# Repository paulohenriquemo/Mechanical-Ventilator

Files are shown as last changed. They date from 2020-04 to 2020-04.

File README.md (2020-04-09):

# Mechanical-Ventilator

Projeto de ventilador emergencial utilizando um Ressucitador manual (AMBU). Conforme o projeto for sendo encaminhado irei atualizando os arquivos.
Nova versão já em fase de testes! Basicamente os mesmos componentes em um layout mais adequado.
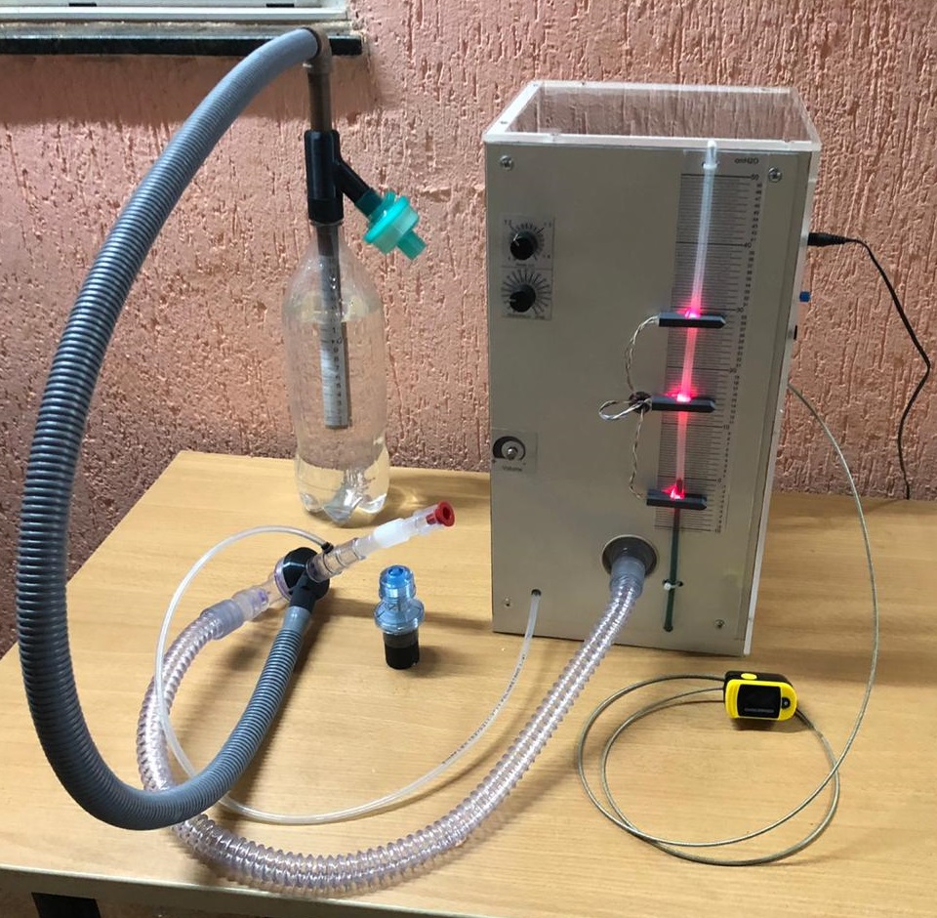
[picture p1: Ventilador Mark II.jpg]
Veltimador_MarkII


Diagrama do sistema:
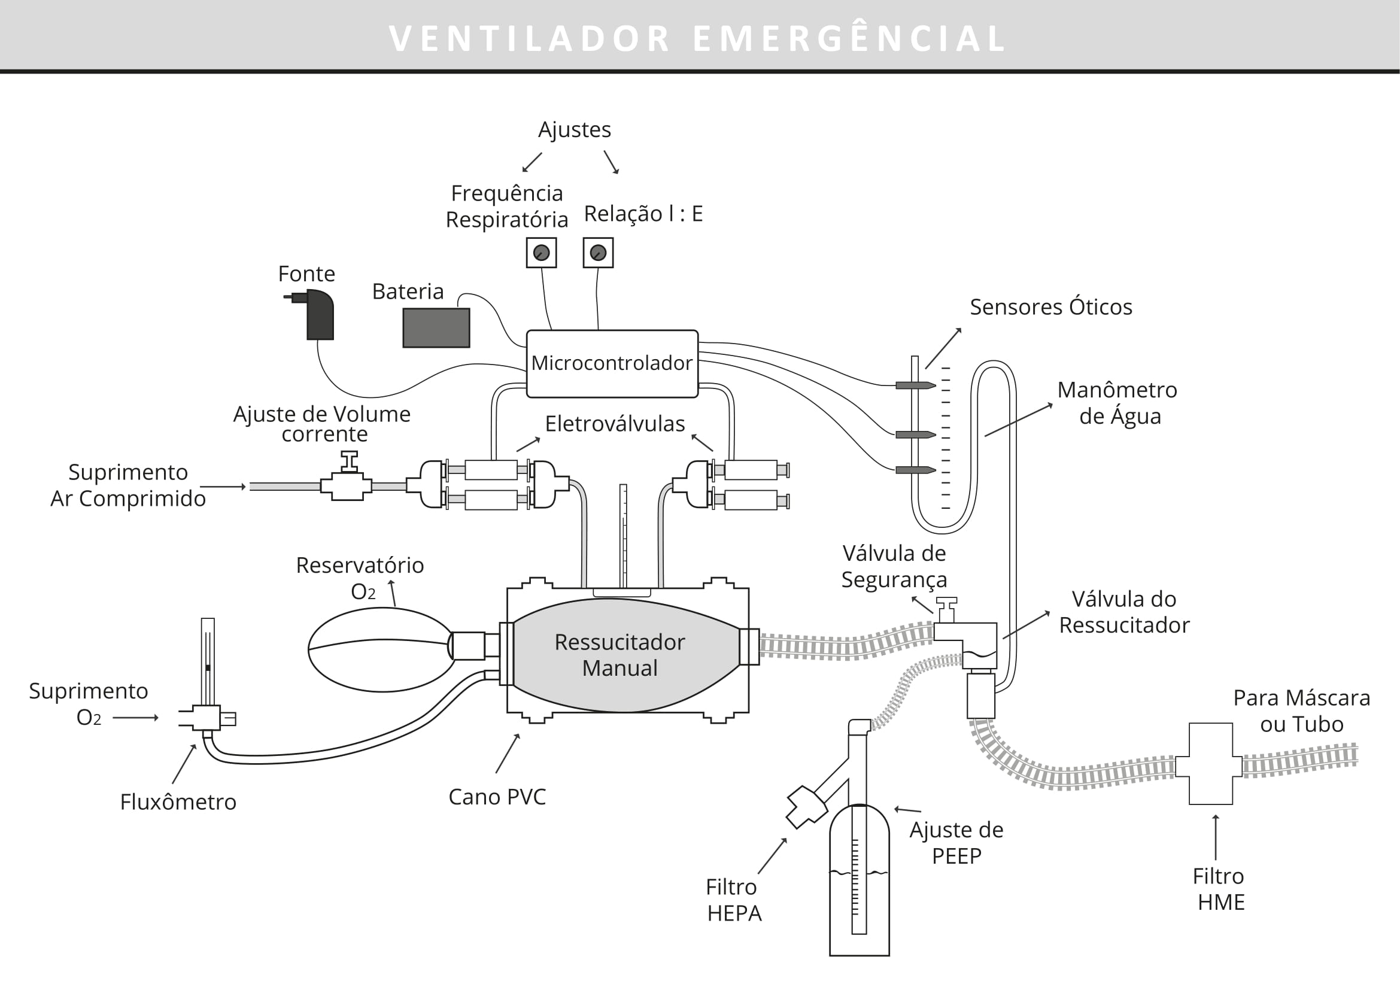
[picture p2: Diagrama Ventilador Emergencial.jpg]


Ilustração de uso:

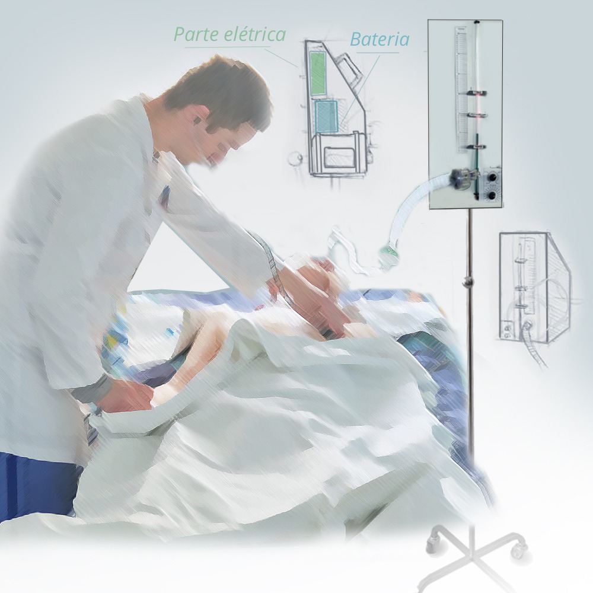
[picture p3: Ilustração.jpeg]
Ilustração de uso


Primeiro protótipo:

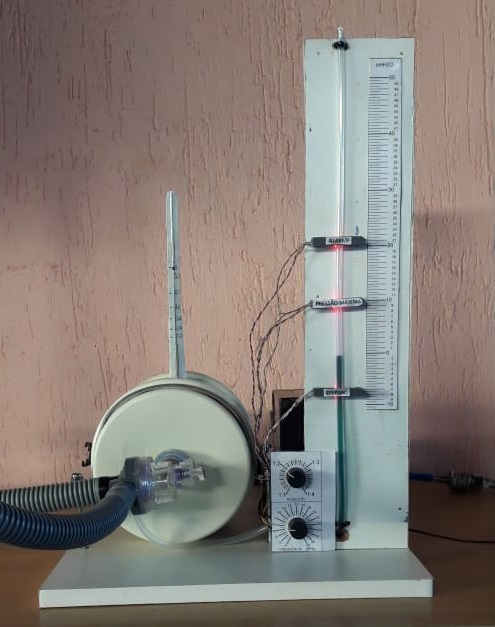
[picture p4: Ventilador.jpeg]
Primeiro Protótipo


Mais detalhes do projeto podem ser vistos no link https://www.youtube.com/watch?v=9hXmWFq5Jxk&feature=youtu.be

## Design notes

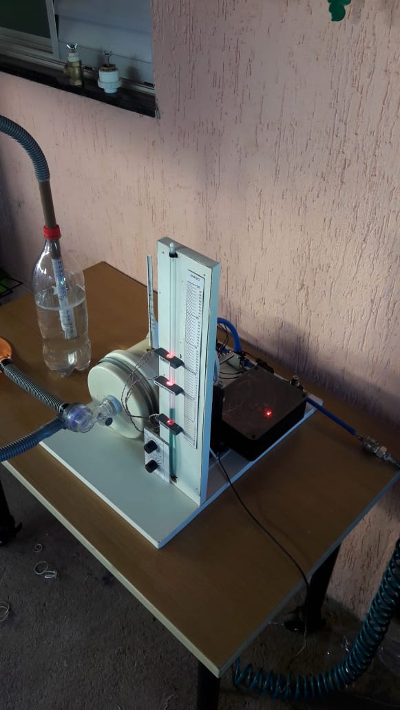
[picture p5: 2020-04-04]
Ventilador 2.jpeg

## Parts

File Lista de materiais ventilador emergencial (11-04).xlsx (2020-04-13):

 | Lista de Materiais para ventilador emergencial
QTD |  | VALOR UNIT | VALOR TOTAL | Referência
1 | AMBU | 230 | 230 | https://magazinemedica.com.br/produtos/visualiza/sku/8049/
1 | Adaptador para válvula PEEP | 30 | 30 | https://www.fibracirurgica.com.br/adaptador-diverter-md-para-conexao-da-valvula-peep-no-ambu/p
1 | Arduino Nano 5V | 25 | 25 | https://produto.mercadolivre.com.br/MLB-1242948735-arduino-nano-v30-5v-atmega328-p-au-_JM?quantity=1
4 | Mosfets | 1 | 4 | https://produto.mercadolivre.com.br/MLB-1321235515-modulo-mosfet-irf520-driver-controlador-p-motor-dc-arduino-_JM?quantity=1
1 | Resistores diversos (Conferir diagrama elétrico) | 2 | 2
4 | LDR 5mm | 0.25 | 1 | https://produto.mercadolivre.com.br/MLB-983516932-100-pecas-fotoresistor-ldr-5mm-pic-arduino-sensor-de-luz-_JM?quantity=1
4 | LED alto brilho vermelho 5mm | 0.1 | 0.4 | https://produto.mercadolivre.com.br/MLB-1433055648-1000x-led-vermelho-alto-brilho-5mm-kit-com-1000-pecas-_JM?quantity=1&variation=50510119992
2 | Potenciometro linear 10k | 1.2 | 2.4 | https://produto.mercadolivre.com.br/MLB-1081635890-potencimetro-10k-linear-com-eixo-l20-estriado-50-unidades-_JM?quantity=1
2 | Knob para potenciometro | 1.9 | 3.8 | https://produto.mercadolivre.com.br/MLB-1324374421-knob-6mm-preto-marcador-branco-p-potencimetro-10-pcs-_JM?quantity=1
1 | fonte 13v 1A | 32 | 32 | https://produto.mercadolivre.com.br/MLB-1305096440-fonte-p-televisor-colorido-13v-13a-bivolt-kairos-tcl1313-_JM?quantity=1
1 | push button pequeno | 1.8 | 1.8 | https://produto.mercadolivre.com.br/MLB-683849365-chave-push-button-na-vermelho-e-preta-pequeno-c10-unidades-_JM?quantity=1
1 | bateria 12V 7AH | 51 | 51 | https://produto.mercadolivre.com.br/MLB-1176479339-bateria-12v-7a-central-de-alarme-e-cerca-eletrica-nobreak-_JM?quantity=1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
1 | CAP 32mm Soldável | 1.5 | 1.5
1 | CAP 20mm Soldável | 0.5 | 0.5
1 | "T" 20mm Soldável | 0.5 | 0.5
1 | Luva de redução 32x35 Soldável | 3.5 | 3.5
1 | O'Ring de Silicone 20mm int por 4 esp | 3 | 3 | https://produto.mercadolivre.com.br/MLB-944957064-kit-oring-silicone-20-mm-especial-rinojosa-_JM?quantity=1
0.018 | tubo pvc soldável 25mm | 3 | 0.054
0.17 | tubo pvc soldável 20mm | 3 | 0.51
0.14 | tubo pvc soldável 32mm | 10 | 1.4
2 | Válvulas Solenoides | 65 | 130 | https://produto.mercadolivre.com.br/MLB-1061583637-solenoide-8mm-12v-vapor-gasolina-gazes-ar-agua-suspenso-_JM?quantity=1
2 | Tubo PU transparente 6mm ou 1/4'' | 2 | 4 | https://produto.mercadolivre.com.br/MLB-1291810963-rolo-de-25m-mangueira-pneumatica-tubo-pu-6mm-transparente-_JM
1 | Tubo PU 8mm | 3.5 | 3.5
1 | Regulador de fluxo 10mm | 14.7 | 14.7
1 | MDF para estrutura com fita de borda | 20 | 20
1 | Acrílico para lateral (45x22,5CM) | 6 | 6
1 | parafuso diversos | 10 | 10
1 | Fio Flexível para as coneções | 5 | 5
4 | Imas cubo 5mm | 0.5 | 2 | https://produto.mercadolivre.com.br/MLB-1335519560-neocube-cubo-magnetico-216-quadrados-im-neodimio-5mm-_JM?quantity=1&variation=44515493831
 | TOTAL |  | 589.564

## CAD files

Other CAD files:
planta respirador (1).dwg

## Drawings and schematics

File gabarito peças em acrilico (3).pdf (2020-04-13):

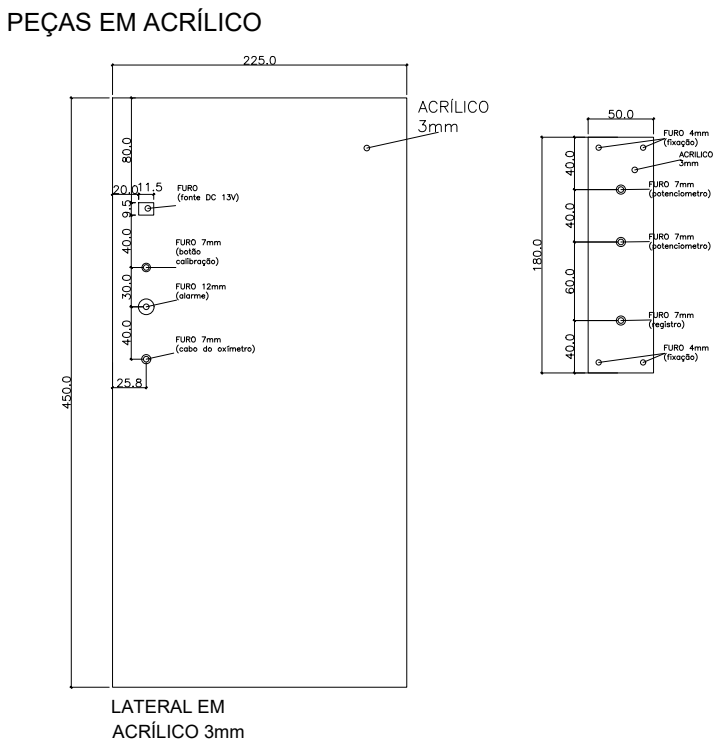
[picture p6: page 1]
LATERAL EM ACRÍLICO 3mm

PEÇAS EM ACRÍLICO

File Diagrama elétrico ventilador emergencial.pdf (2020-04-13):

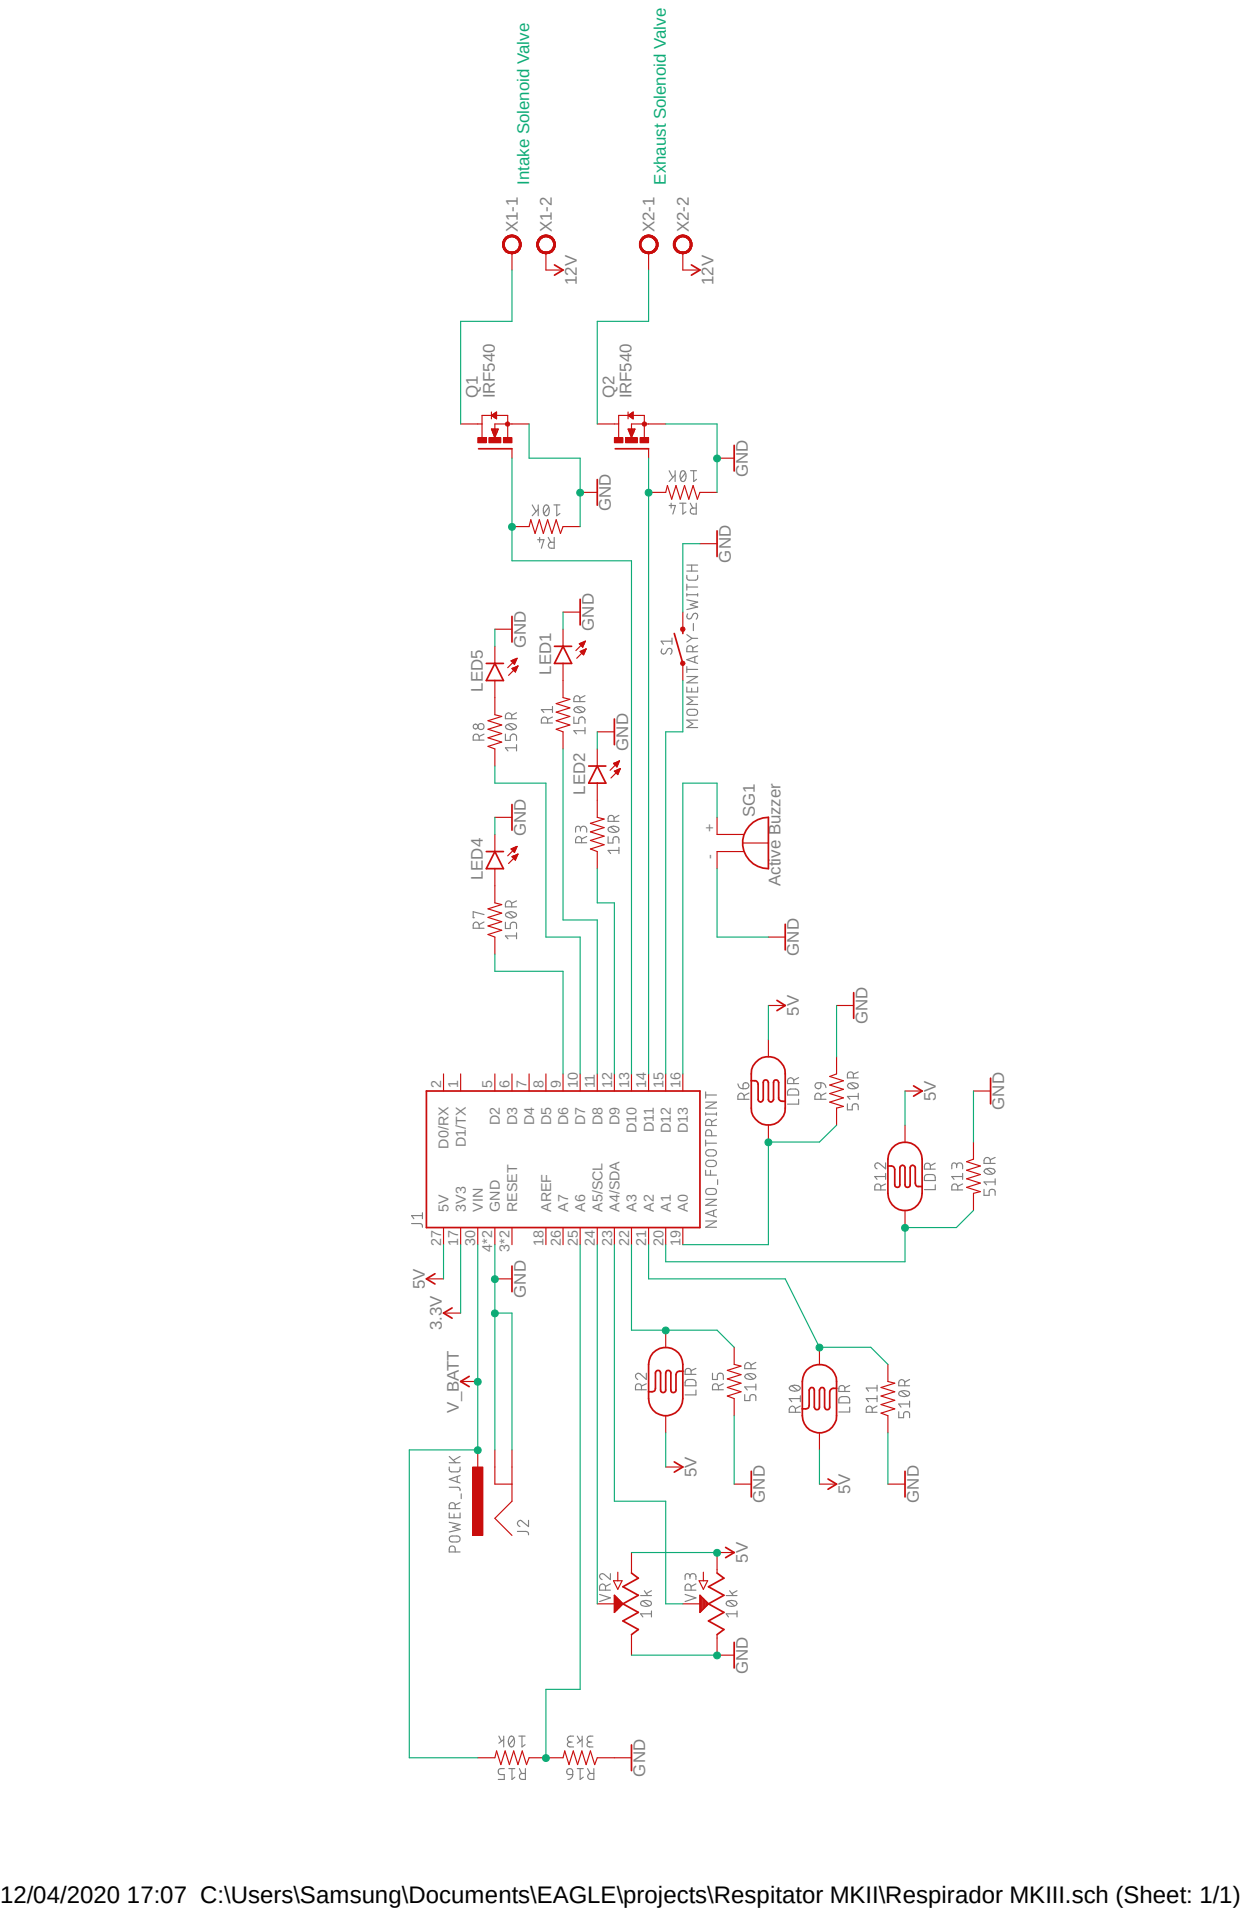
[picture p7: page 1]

9 D7 10 D8 11 D9 12 D10 13 D11 14 D12 15 VIN 30 5V 27 A0 19 A1 20 A2 21 A3 22 A4/SDA 23 A5/SCL 24 A6 25 A7 26 AREF 18 3V3 17 D13 16 Q1 X1-1 X1-2 Q2 X2-1 X2-2 - + SG1 LED4 LED1 LED5 LED2 Intake Solenoid Valve Exhaust Solenoid Valve

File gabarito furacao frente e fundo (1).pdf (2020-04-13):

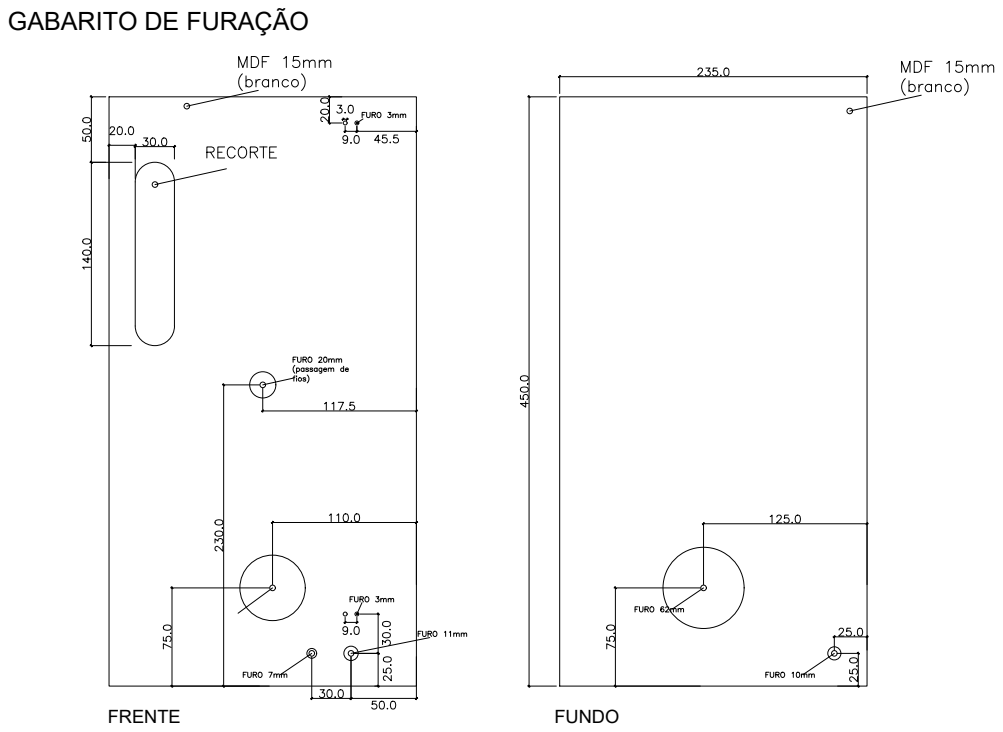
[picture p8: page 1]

GABARITO DE FURAÇÃO

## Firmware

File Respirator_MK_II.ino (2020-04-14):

// ****************************************** Inputs and outputs configuration **************************************************


int StartInspirationPin = A0;    // select the input pin for the StartInspiration sensor (LDR)
int MinPressurePin = A1;            // select the input pin for the Minimum pressure sensor (LDR)
int MaxPressurePin = A2;    // select the input pin for the EndInspiration sensor (LDR)
int HighPressurePin = A3;    // select the input pin for the High Pressure sensor (LDR)
int PotentiometerRateIEPin = A4;    // select the input pin for the potentiometer that adjust the inspiration/expiration rate
int PotentiometerRatePin = A5;    // select the input pin for the potentiometer that adjust the respiratory rate
int SupplyVoltagePin = A7;          // Select input pin for monitoring Supply voltage

int SwitchPin = 12;               // select the input pin for the Calibration Switch
int AlarmPin = 13;               // select one output pin for Alarm. ( Some Buzzer, light or Both )
int IntakePin = 10;      // select the output pin for the intake solenoid
int ExhaustPin = 11;    // select the output pin for the exhaust solenoid
int LedHPPin = 7;    // select the output pin for LED that iluminate de StartInspiration sensor (LDR)
int LedEIPin = 6;    // select the output pin for LED that iluminate de EndInspiration sensor (LDR)
int LedMPPin = 5;    // select the output pin for LED that iluminate de High Pressure sensor (LDR)
int LedSIPin = 4;    // select the output pin for LED that iluminate de Minimum Pressure sensor (LDR)

// ****************************************** Variables used in the code **************************************************

int PotentiometerValue = 0;  // variable to store the value coming from the potentiometer
float RespiratoryRate = 10; // variable to store the value of Respiratory Rate in Breaths per minute
int RespiratoryTime = 5000; // variable to store the value of Respiratory Time in miliseconds
int InsuficientPressureError = 0;   // variable to Count the number of cycles that desired pressure was not reached
int HighPressureError = 0;          // variable to Count the number of times that High Pressure sensor has triggered
int treshold_StartInspiration = 177;      //  Adjust With serial Monitor
int treshold_MinPressure = 417;          //  Adjust With serial Monitor
int treshold_MaxPressure = 407 ;        //  Adjust With serial Monitor
int treshold_HighPressure = 495 ;      //  Adjust With serial Monitor
int treshold_SupplyVoltage = 928 ;    //  Adjust With serial Monitor

unsigned long  CicleTime = 0;
unsigned long InspiratoryTime = 0;
float RateIE = 50;
boolean flag_StartInspiration = 0;
boolean flag_EndInspiration = 0;
boolean flag_HighPressure = 0;
boolean flag_DetectPressure = 1;
boolean flag_DetectTimeout = 1;

boolean calibration_complete = 0;
boolean Switch = 0;
boolean AlarmState = 0;



// ****************************************** Setup **************************************************

void setup() {
// Serial.begin (9600);

  pinMode(AlarmPin, OUTPUT);
  pinMode(ExhaustPin, OUTPUT);
  pinMode(IntakePin, OUTPUT);
  pinMode(LedSIPin, OUTPUT);
  pinMode(LedEIPin, OUTPUT);
  pinMode(LedHPPin, OUTPUT);
  pinMode(LedMPPin, OUTPUT);
  pinMode(SwitchPin, INPUT_PULLUP);
 digitalWrite(LedSIPin, HIGH); 
 digitalWrite(LedEIPin, HIGH); 
 digitalWrite(LedHPPin, HIGH); 
 digitalWrite(LedMPPin, HIGH);
 digitalWrite(AlarmPin, HIGH);
 delay(800);
 digitalWrite(AlarmPin, LOW);
 delay(200);


}

void loop() {


// ****************************************** Use Serial Monitor only for debug than disable **************************************************

  

//   delay(500);
//  Serial.print ("Start Inspiration "); Serial.println (analogRead (StartInspirationPin));
//  Serial.print ("Min Pressure "); Serial.println (analogRead (MinPressurePin));
//  Serial.print ("Max Pressure "); Serial.println (analogRead (MaxPressurePin));
//  Serial.print ("High Pressure "); Serial.println (analogRead (HighPressurePin));
//Serial.print ("Bateria "); Serial.println (analogRead (A7));

//  Serial.println ();
 


// ****************************************** Read Sensors and potentiometer **************************************************


if ((millis() - CicleTime) > ( 0.5 * RespiratoryTime)) {                                // Condition to avoid multiple flag trigger 
  if (analogRead (StartInspirationPin) > treshold_StartInspiration){                   // Check if Start Inspiration sensor has triggered
     flag_StartInspiration = 1;
     digitalWrite(LedSIPin, LOW);
  delay(200);
  digitalWrite(LedSIPin, HIGH);
      }}
if(flag_DetectPressure){
if (analogRead (MaxPressurePin) < treshold_MaxPressure){                          // Check if End Inspiration sensor has triggered
  digitalWrite(LedEIPin, LOW); 
  flag_EndInspiration = 1;
  flag_DetectPressure = 0;
 
} 
}
  

 if (analogRead (HighPressurePin) < treshold_HighPressure){                        // Check if High Pressure sensor has triggered
  digitalWrite(IntakePin, LOW);                                                   // Close Intake Solenoid
 digitalWrite(ExhaustPin, HIGH);                                                 // Open Exhaust Solenoid
  digitalWrite(LedHPPin, LOW);
  delay(150);
  digitalWrite(LedHPPin, HIGH);
digitalWrite(AlarmPin, HIGH);
  delay(1000);
  digitalWrite(AlarmPin, LOW);
  
  }




 PotentiometerValue = analogRead(PotentiometerRatePin);
 RespiratoryRate = map(PotentiometerValue,0,1023,40,400);             // Ajust the scale of potentiometer




 RespiratoryTime = (60000 / RespiratoryRate)*10 ;                        // Calculates the time for each cicle in milliseconds
 
 PotentiometerValue = analogRead(PotentiometerRateIEPin); 
 RateIE = map(PotentiometerValue,0,1024,2000,5000);             // Ajust the scale of potentiometer

 
InspiratoryTime = (RespiratoryTime / RateIE * 1000);                     // Calculates the inspiratory time for each cicle in milliseconds






// ****************************************** Execute respiratory cicle **************************************************




  
 if((millis() - CicleTime) > RespiratoryTime ) {                      // Start Inspiration cicle if "flag_StartInspiration" has not been triggered  (Timeout)
  flag_StartInspiration = 1;
 }
 


if(flag_StartInspiration) {
  
digitalWrite(IntakePin, HIGH);                                 // Open Intake Solenoid
digitalWrite(ExhaustPin, LOW);                                // Close exaust Solenoid in case of "flag_EndExpiration" has not been Triggered
CicleTime = millis();
flag_StartInspiration = 0;
flag_DetectPressure = 1;
flag_DetectTimeout = 1;

}
if(flag_DetectTimeout){
if((millis() - CicleTime) > InspiratoryTime) {         // End Inspiration Cicle if "flag_EndInspiration" has not been Triggered
  flag_EndInspiration = 1;
}
}


if(flag_EndInspiration) {
  
digitalWrite(IntakePin, LOW);                                // Close Intake Solenoid
digitalWrite(ExhaustPin, HIGH);                              // Open Exhaust Solenoid
flag_EndInspiration = 0;
flag_DetectTimeout = 0;
delay(150);
digitalWrite(LedEIPin, HIGH);                              // turn de LED on for the next cicle

 if (analogRead (MinPressurePin) < treshold_MinPressure){      // Acidental disconection alarm reset
  digitalWrite(AlarmPin, LOW);
  }


if (analogRead (MinPressurePin) > treshold_MinPressure){      // Acidental disconection alarm
  digitalWrite(AlarmPin, HIGH);
  digitalWrite(LedMPPin, LOW);
  delay(250);
  digitalWrite(LedMPPin, HIGH);
   }

if (analogRead (SupplyVoltagePin) < treshold_SupplyVoltage){                        // Check the Battery Voltage
  digitalWrite(AlarmPin, HIGH);
  delay(200);
  digitalWrite(AlarmPin, LOW);}

  
}



  
// ****************************************** Calibrate LDR Sensors  **************************************************



if (digitalRead(SwitchPin) == LOW) {                  
  digitalWrite (AlarmPin, HIGH);
  delay(1000);
   digitalWrite (AlarmPin, LOW);
   delay (500);


  

int Max_StartInspiration;
int Min_StartInspiration;
int Max_MinPressure;
int Min_MinPressure;
int Max_MaxPressure;
int Min_MaxPressure;
int Max_HighPressure;
int Min_HighPressure;

Max_StartInspiration = analogRead (StartInspirationPin);
Max_MinPressure = analogRead (MinPressurePin);
Max_MaxPressure = analogRead (MaxPressurePin);
Max_HighPressure = analogRead (HighPressurePin);

  digitalWrite (AlarmPin, HIGH);
  delay(200);
   digitalWrite (AlarmPin, LOW);
   digitalWrite(LedEIPin, LOW); 
   digitalWrite(LedSIPin, LOW);
   digitalWrite(LedMPPin, LOW);
   digitalWrite(LedHPPin, LOW);
   delay(200);   
   digitalWrite(LedEIPin, HIGH); 
   digitalWrite(LedSIPin, HIGH);
   digitalWrite(LedMPPin, HIGH);
   digitalWrite(LedHPPin, HIGH);

 delay(10000);


Min_StartInspiration = analogRead (StartInspirationPin);
Min_MinPressure = analogRead (MinPressurePin);
Min_MaxPressure = analogRead (MaxPressurePin);
Min_HighPressure = analogRead (HighPressurePin);



treshold_StartInspiration = (Max_StartInspiration + Min_StartInspiration) / 2;
treshold_MinPressure = (Max_MinPressure + Min_MinPressure) / 2;
treshold_MaxPressure = (Max_MaxPressure + Min_MaxPressure) / 2;
treshold_HighPressure = (Max_HighPressure + Min_HighPressure) / 2 ;


   digitalWrite(LedEIPin, LOW); 
   digitalWrite(LedMPPin, LOW);
   digitalWrite(LedSIPin, LOW);
   digitalWrite(LedHPPin, LOW);
   delay(200);   
   digitalWrite(LedEIPin, HIGH); 
   digitalWrite(LedMPPin, HIGH);
   digitalWrite(LedSIPin, HIGH);
   digitalWrite(LedHPPin, HIGH);
   digitalWrite (AlarmPin, HIGH);
   delay(100);
   digitalWrite (AlarmPin, LOW);
   delay(400);
   digitalWrite (AlarmPin, HIGH);
   delay(100);
   digitalWrite (AlarmPin, LOW);
   delay(400);
   digitalWrite (AlarmPin, HIGH);
   delay(100);
   digitalWrite (AlarmPin, LOW);
   delay (8000);
   
  }

}
